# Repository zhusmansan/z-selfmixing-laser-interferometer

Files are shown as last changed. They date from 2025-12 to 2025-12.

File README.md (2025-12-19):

# Драйвер для лазера и усилитель фотодиода для самосмешиваюей интерферометрии(self-mixing interferometry, [SMI](https://en.wikipedia.org/wiki/Self-mixing_interferometry)).

Воспроизведён эксперимент [Laser diode self-mixing: Range-finding and sub-micron vibration measurement](https://www.youtube.com/watch?v=MUdro-6u2Zg)

## Схема драйвера\усилителя

1) Фильтры питания и стабилизатор 5в
2) Регулируемый источник постоянного тока
3) Трансимпедансный усилитель сигнала фотодиода с регулируемым усилением
4) Дополнительная ступень усиления х10

 Схему для KiCad можно посмотреть в соответствующей [папке](./z-selfmixing-laser-interferometer-kicad/)

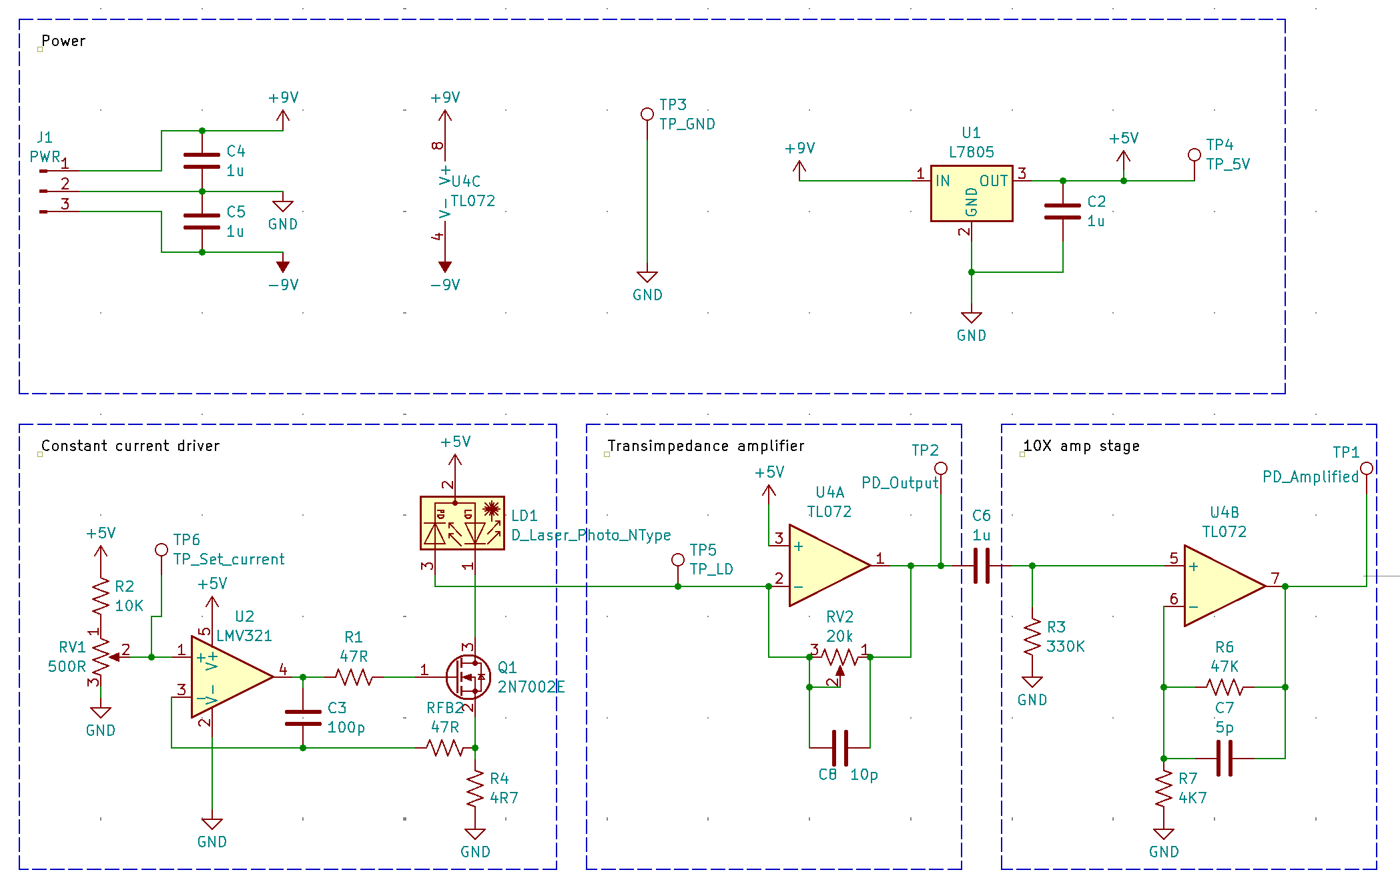
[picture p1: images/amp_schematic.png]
Схема

Номиналы фильтрующих конденсаторов выбраны при помощи ГПСЧ.

## Печатная плата

Плата односторонняя, произведена методом лазерного экспонирования фоторезиста.

Травление -- 1 флакон перекиси водорода, 20г лимонной кислоты, чайная ложка поваренной соли. Для ускорения травления, раствор подогреть в микроволновой печи.

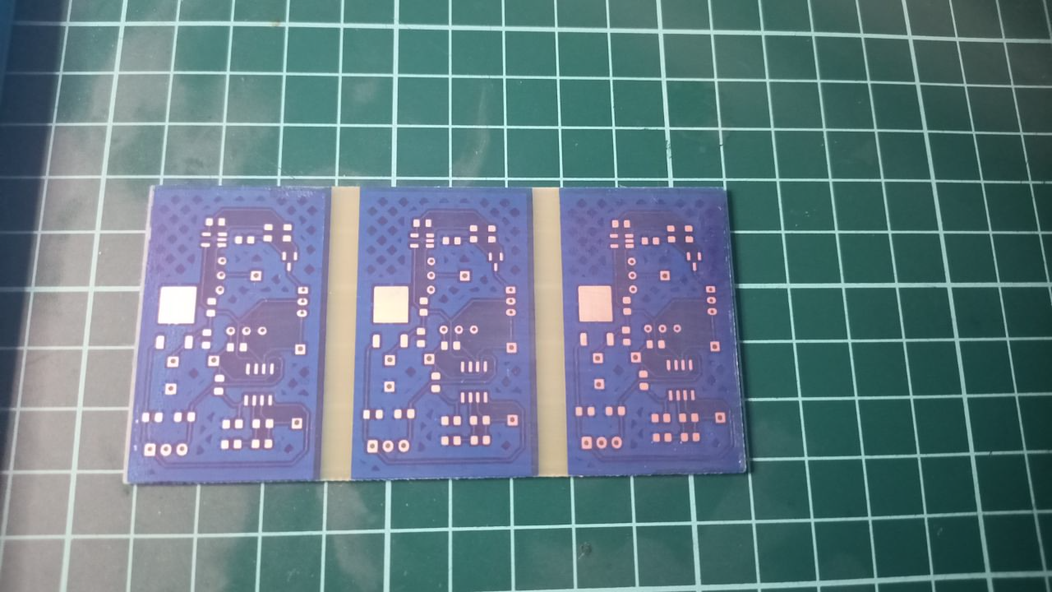
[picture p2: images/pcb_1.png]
Печатная плата


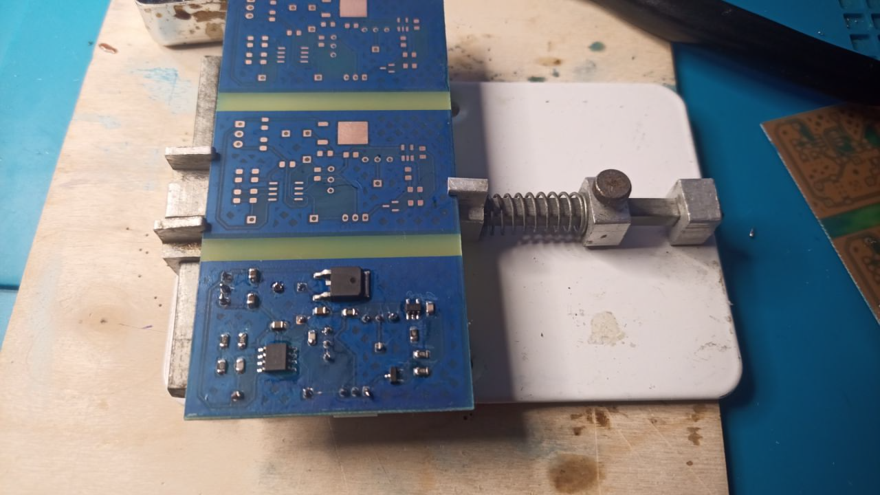
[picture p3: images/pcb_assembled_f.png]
Собранная печатная плата, верх


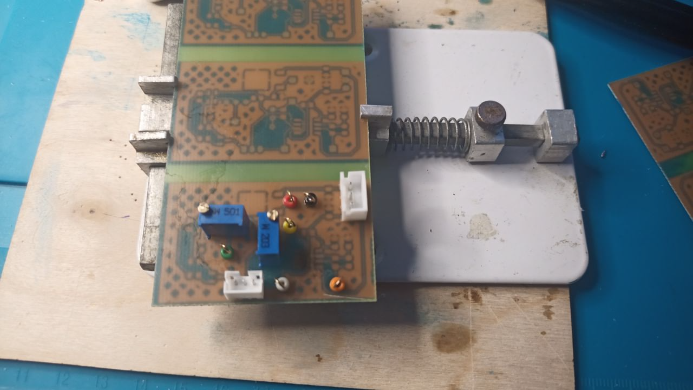
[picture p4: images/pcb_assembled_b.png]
Собранная печатная плата, низ


Питание устройства от 2х 9в батареек. Удобный бесшумный источник питания для весьма чувствительного усилителя.

## Установка

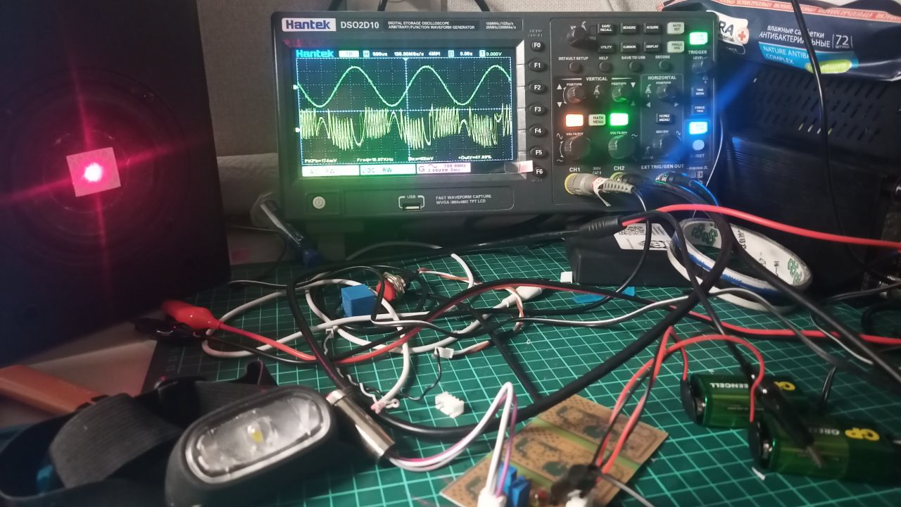
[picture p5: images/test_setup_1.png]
Общий вид установки


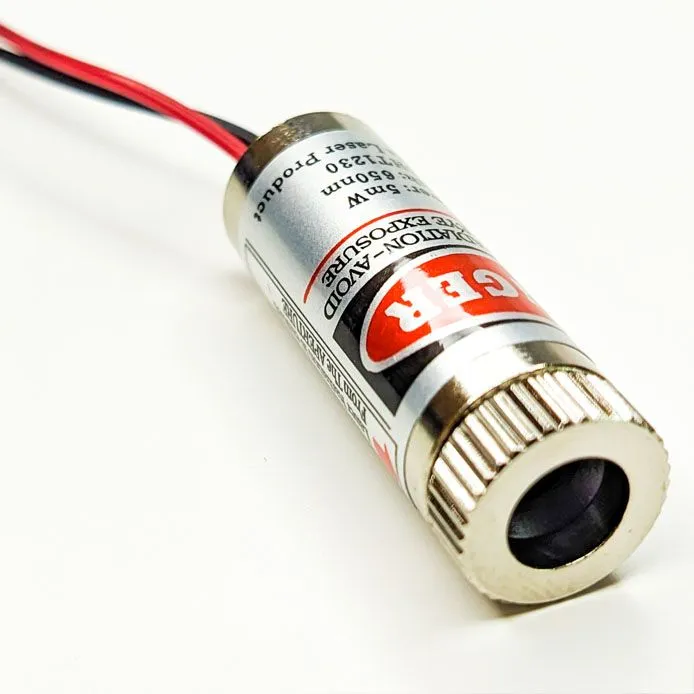
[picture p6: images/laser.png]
cht-1230
  1) Лазер со встроенным фотодиодом контроля мощности. Использован дешёвый лазер с фокусирующей оптикой типа: 
  Электроника управления лазером удалена, пины лазерного диода и фотодиода выведены наружу, через разъём типа JST_PH(3).

  2) Усилитель запитан от 2 элементов типа крона.

  3) Лазер направлен на мембрану динамика с наклеенной световозвращающей лентой. Динамик приводится в действие генератором сигнала, встроенным в осциллограф.

## Результат

На осцилограмме: зелёная линия -- сигнал подаваемый на динамик, жёлтая линия -- осцилограмма интерферометрического сигнала.
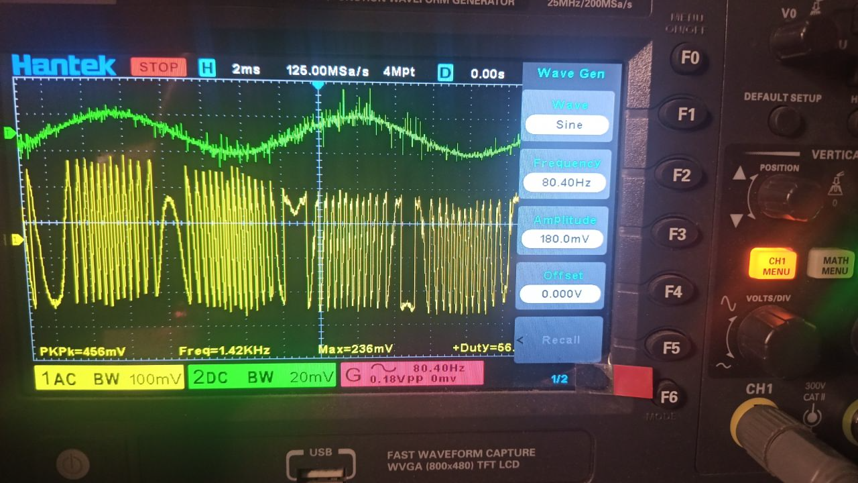
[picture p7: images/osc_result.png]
Осцилограмма


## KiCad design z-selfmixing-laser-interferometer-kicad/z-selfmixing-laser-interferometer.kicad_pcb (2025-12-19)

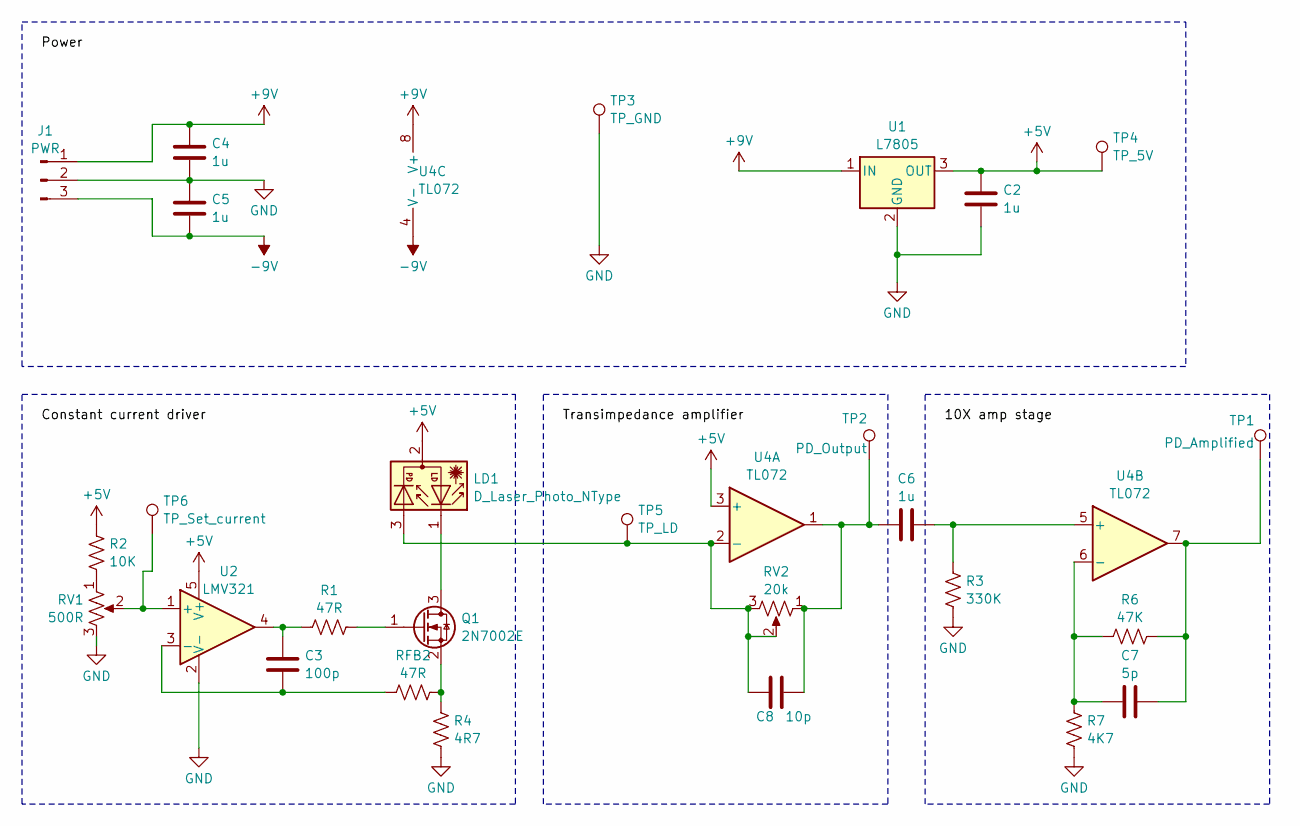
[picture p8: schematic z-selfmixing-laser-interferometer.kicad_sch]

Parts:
C2, C4, C5, C6: 1u; C_0805_2012Metric_Pad1.18x1.45mm_HandSolder
C3: 100p; C_0805_2012Metric_Pad1.18x1.45mm_HandSolder
C7: 5p; C_0805_2012Metric_Pad1.18x1.45mm_HandSolder
C8: 10p; C_0805_2012Metric_Pad1.18x1.45mm_HandSolder
J1: PWR; JST_XH_B3B-XH-A_1x03_P2.50mm_Vertical
LD1: D_Laser_Photo_NType; JST_PH_B3B-PH-K_1x03_P2.00mm_Vertical
Q1: 2N7002E; SOT-23
R1: 47R; R_0805_2012Metric_Pad1.20x1.40mm_HandSolder
R2: 10K; R_0805_2012Metric_Pad1.20x1.40mm_HandSolder
R3: 330K; R_0805_2012Metric_Pad1.20x1.40mm_HandSolder
R4: 4R7; R_0805_2012Metric_Pad1.20x1.40mm_HandSolder
R6: 47K; R_0805_2012Metric_Pad1.20x1.40mm_HandSolder
R7: 4K7; R_0805_2012Metric_Pad1.20x1.40mm_HandSolder
RFB2: 47R; R_0805_2012Metric_Pad1.20x1.40mm_HandSolder
RV1: 500R; Potentiometer_Bourns_3296W_Vertical
RV2: 20k; Potentiometer_Bourns_3296W_Vertical
TP1: PD_Amplified; PinHeader_1x01_P2.54mm_Vertical
TP2: PD_Output; PinHeader_1x01_P2.54mm_Vertical
TP3: TP_GND; PinHeader_1x01_P2.54mm_Vertical
TP4: TP_5V; PinHeader_1x01_P2.54mm_Vertical
TP5: TP_LD; PinHeader_1x01_P2.54mm_Vertical
TP6: TP_Set_current; PinHeader_1x01_P2.54mm_Vertical
U1: L7805; TO-252-2
U2: LMV321; SOT-23-5_HandSoldering
U4: TL072; SO-8_3.9x4.9mm_P1.27mm

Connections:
+5V: C2.1, LD1.2, R2.1, TP4.1, U1.3 (OUT), U2.5 (V+), U4.3 (+)
+9V: C4.1, J1.1, U1.1 (IN), U4.8 (V+)
-9V: C5.2, J1.3, U4.4 (V-)
GND: C2.2, C4.2, C5.1, J1.2, R3.2, R4.2, R7.2, RV1.3, TP3.1, U1.2 (GND), U2.2 (V-)
unnamed: C3.1, R1.1, U2.4
unnamed: C6.1, C8.2, RV2.1, TP2.1, U4.1
unnamed: C7.2, R6.2, TP1.1, U4.7
unnamed: LD1.1, Q1.3 (D)
unnamed: Q1.1 (G), R1.2
unnamed: Q1.2 (S), R4.1, RFB2.1
unnamed: R2.2, RV1.1
unnamed: RV1.2, TP6.1, U2.1 (+)
unnamed: C3.2, RFB2.2, U2.3 (-)
unnamed: C8.1, LD1.3, RV2.2, RV2.3, TP5.1, U4.2 (-)
unnamed: C6.2, R3.1, U4.5 (+)
unnamed: C7.1, R6.1, R7.1, U4.6 (-)

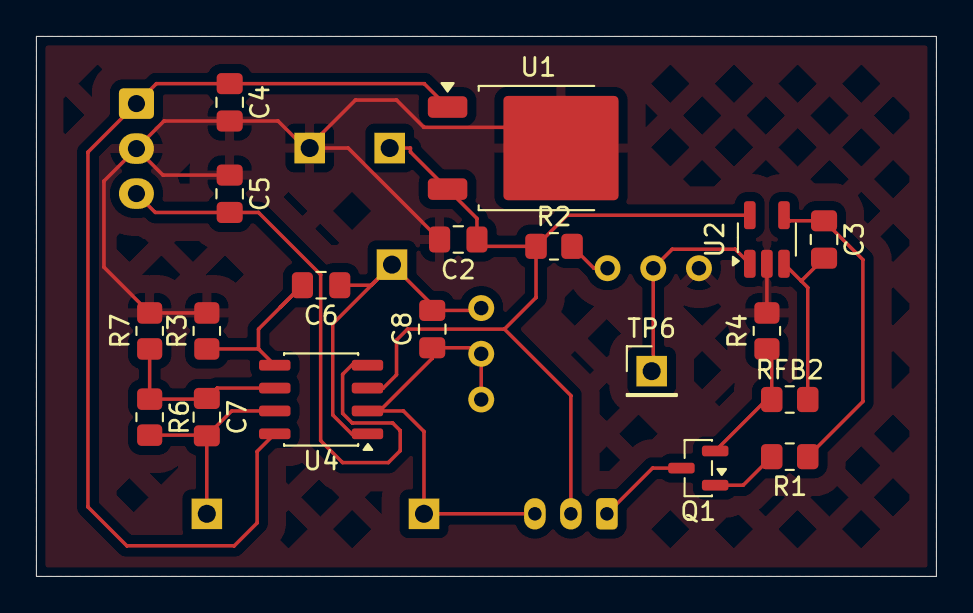
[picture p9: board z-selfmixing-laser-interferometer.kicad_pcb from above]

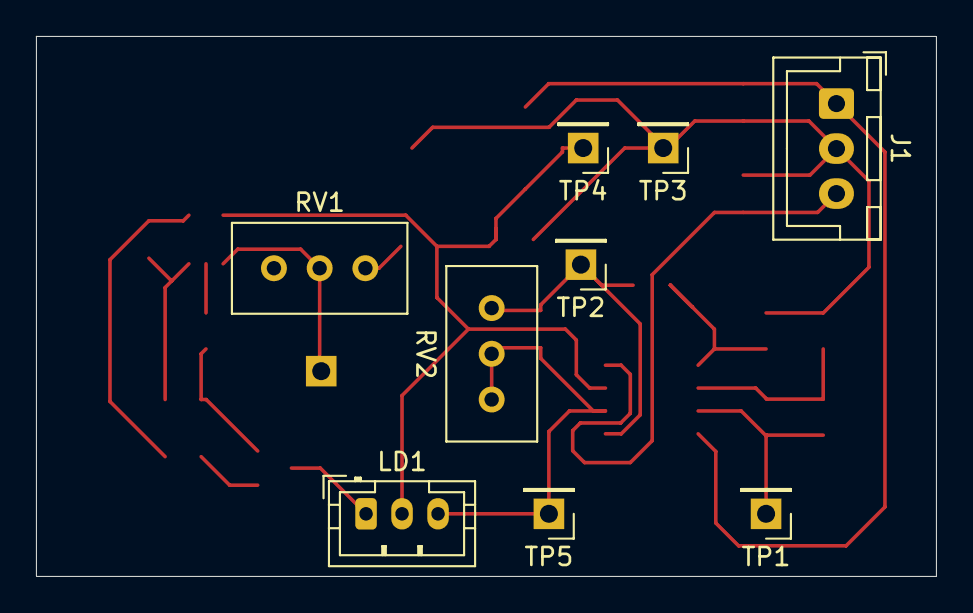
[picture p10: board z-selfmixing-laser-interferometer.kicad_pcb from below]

Board: 2 copper layers, 50.0 x 30.0 mm, 28 parts (9 on the bottom side), 16 nets.

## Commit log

2025-12-19 Описание проекта
    [z-selfmixing-laser-interferometer.kicad_pcb, z-selfmixing-laser-interferometer.kicad_sch]
2025-12-19 лишние файлы --
2025-12-19 +гитигнор
